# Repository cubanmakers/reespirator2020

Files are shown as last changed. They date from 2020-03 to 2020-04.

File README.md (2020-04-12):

# Reespirator 2020

Este repositorio pretende documentar y organizar los pasos para fabricar prototipos de  **Reespirator-2020**, un respirador open-source basado en el sistema de ventilación mecánica Jackson-Rees, diseñado y mejorado a partir de los prototipos elaborados por el equipo de Reesistencia Team para todas aquellas personas, organizaciones o empresas que quieran fabricarlo en cualquier parte del mundo.  

> ESTA DOCUMENTACIÓN ESTÁ EN ELABORACIÓN, COMPRUEBE REGULARMENTE LOS CAMBIOS, LAS PRIMERAS VERSIONES PUBLICADAS ESTÁN DESACTUALIZADAS. 

## Disclaimer
*Recuerde que un respirador es un dispositivo médico que sólo puede ser utilizado por personal cualificado y que un mal respirador o un respirador mal utilizado puede matar.*

La presente documentación **NO PERMITE CONSTRUIR UN RESPIRADOR FINAL**, sólo se publica para que se pueda fabricar PROTOTIPOS para investigación. 

## Info
*¿Qué es Reespirator 2020?*

El dispositivo Reespirator 2020 es un prototipo de sistema respirador de emergencia con elementos disponibles por la mayoría de las personas en cualquier parte del mundo, de rápida construcción y con la capacidad para mantener constantes ventilatorias aceptables en un paciente afecto de [Síndrome de Distrés Respiratorio Agudo](https://es.wikipedia.org/wiki/S%C3%ADndrome_de_dificultad_respiratoria_aguda) o SDRA.

Aunque el origen de Reespirator es España, debido a las regulaciones y validaciones necesarias para los productos médicos, y aunque Reespirator 23 de Reesistencia Team en el que se ha basado este nuevo diseño, ha superado varias pruebas preclínicas con animales, y de compatibilidad electromagnética, suponemos que este dispositivo nunca se llegará a fabricar masivamente en España, dónde afortunadamente lo peor de la crisis del COVID-19 parece que ya ha pasado (08/04/20); esperamos que este y otros diseños puedan ser útiles en otros países.

Aún así no nos damos por vencidos y seguiremos desarrollando el proyecto al menos en 2 versiones:

* Versión low cost (basada en Arduino y con caja de metacrilato, madera...)
* Versión pro (con un autómata PLC + un HMI y caja de chapa plegada en acero inoxidable)

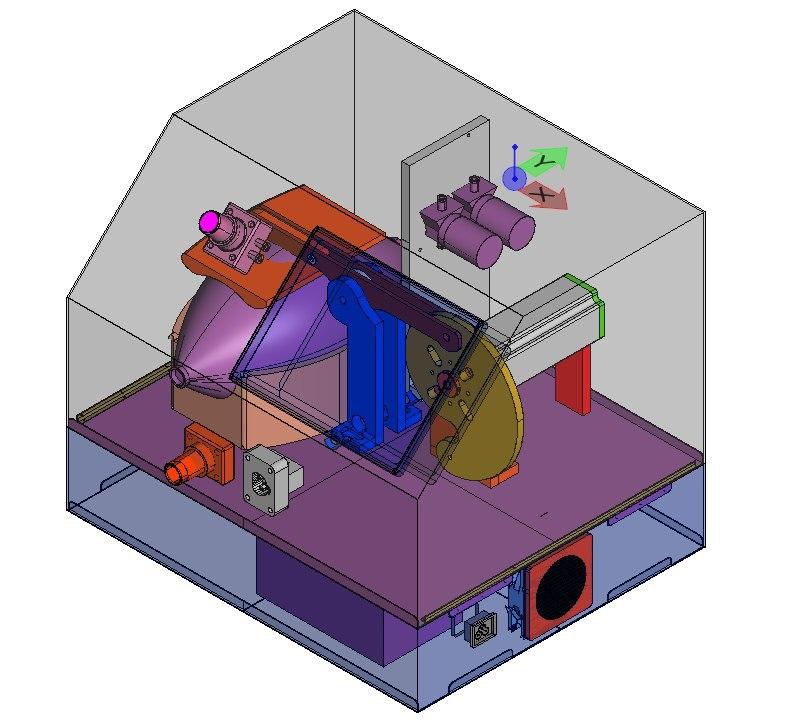
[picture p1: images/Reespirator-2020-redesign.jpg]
Reespirator


## Primeros pasos
Antes de montar un respirador lea toda la documentación posible e infórmese bien, si necesitas alguna aclaración abra un Issue y lo corregiremos en cuanto podamos. Si crees que puedes mejorar el diseño o el código envíanos un Pull request.

## [Estructura básica](https://gitlab.com/reespirator/reespirator-doc/-/blob/master/CASE.md)
Reespirator 2020 consta de una [caja](https://gitlab.com/reespirator/reespirator-doc/-/blob/master/CASE.md) diseñada para fabricarse mediante corte láser que contiene casi todos elementos del respirador en su interior. En el prototipo actual las piezas del prototipo se han diseñado para su corte por láser en metacrilato si bien la imagen anterior corresponde a la nueva evolución que podrá fabricarse también con chapa plegada.

## [Sistema neumático](https://gitlab.com/reespirator/reespirator-doc/-/blob/master/NEUMATIC.md)
El [sistema neumático](https://gitlab.com/reespirator/reespirator-doc/-/blob/master/NEUMATIC.md) del Reespirator 2020 está basado en un sistema Jackson-Rees. Reespirator 2020 utiliza además una serie de válvulas, sensores de presión y caudal y tubuladuras para hacer llegar al aire a los pulmones del paciente.

## [Mecánica](https://gitlab.com/reespirator/reespirator-doc/-/blob/master/MECHANIC.md)
El [sistema mecánico](https://gitlab.com/reespirator/reespirator-doc/-/blob/master/MECHANIC.md) pretende realizar los movimientos necesarios para realizar las maniobras de inspiración y espiración forzada del paciente mediante elementos mecánicos sustituyendo al personal humano que utilizaría el sistema de ventilación.

## [Electrónica](https://gitlab.com/reespirator/reespirator-doc/-/blob/master/ELECTRONICS.md)
La [electrónica](https://gitlab.com/reespirator/reespirator-doc/-/blob/master/ELECTRONICS.md) de control gestiona el movimiento del motor y los sensores que permiten realizar un control de lazo cerrado automatizado del sistema.
Además de la electrónica de control se emplea una electrónica adicional como interfaz de usuario que permite monitorizar diferentes señales del respirador y modificar en tiempo real diferentes configuraciones del mismo.

## [Firmware](https://gitlab.com/reespirator/reespirator-doc/-/blob/master/FIRMWARE.md)
El sistema de control necesita ser programado con un [firmware](https://gitlab.com/reespirator/reespirator-doc/-/blob/master/FIRMWARE.md) que permita hacer funcionar el dispositivo. Dicho programa se ha realizado conforme a las especificaciones de los especialistas médicos para realizar las funciones para las que el dispositivo fue diseñado.

## [Manual de usuario](https://gitlab.com/reespirator/reespirator-doc/-/blob/master/MANUAL.md)
El dispositivo Reespirator 2020 es un dispositivo médico y su uso sólo debe realizarse por personal especializado. Ofrecemos aquí un breve [manual de uso](https://gitlab.com/reespirator/reespirator-doc/-/blob/master/MANUAL.md) del mismo; pero es el personal sanitario el que sabe los parámetros que deben utilizarse para el tratamiento del paciente.

## Historia y principales cambios de esta versión

El proyecto Reespirator2020 toma como punto de partida el proyecto Reespirator 23 (o 24) v3 de **Reesistencia Team** a partir del cual realizamos un fork.

En esta nueva versión se incluyen principalmente los siguientes cambios:

 - Revisión y reestructuración en profundidad del códido de Arduino para asegurar la robustez de funcionamiento en todos los supuestos.
 - La recuperación del interfaz básico con LCD de 20x04 y elementos sencillos de control (4 pulsadores y un encoder con pulsador).
 - Establecimiento y documentación de una interfaz de comunicación serie que permite la utilización de sistemas (en adelante llamados Display+) de visualización, control y conectividad, que pueden ser utilizados como accesorios para aportar mejor usabilidad al sistema.
 - Se trabaja para estandarizar y popularizar los sensores y electro-válvulas para utilizar partes (comerciales o diseñadas) posibles de conseguir con la situación de emergencia actual y a precios accesibles.

## Repositorio temporal de trabajo para el código de Reespirator2020

El siguiente repositorio se está utilizando como fork de trabajo para transformar el código de Respirator 23 (o 24) v3 de Reesistencia Team (cuyo código se denominó 'batalla') en el código estable que se usará en Respirator 2020 de arduino, cuyo código se denominó  ['retaguardia'](https://gitlab.com/reespirator-arduino).

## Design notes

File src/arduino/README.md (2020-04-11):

# Reespirator

En la carpeta **rees_firmware** está el código de la última versión utilizada en Reespirator 23 para Arduino y la Beagle Bone con una pantalla táctil de 7" de WaveShare.

En la carpeta **test** encontrarás scripts de código que se utilizaron para hacer pruebas de distintos módulos y sensores utilizados en los primeros prototipos del Reespirator 23

## Resources

* [Arduino Reference](https://www.arduino.cc/reference/en/)
* [Arduino Best Practices and Gotchas](https://www.theatreofnoise.com/2017/05/arduino-ide-best-practices-and-gotchas.html)
* [C++ Best Practices (Gitbook)](https://lefticus.gitbooks.io/cpp-best-practices/content/)

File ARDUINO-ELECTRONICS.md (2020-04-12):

***Este documento describe la electrónica basada en Arduino. Si desea ver la versión para PLC, está disponible en el siguiente enlace: https://gitlab.com/reespirator/reespirator2020/-/blob/master/PLC-ELECTRONICS.md***

## Electrónica basada en Arduino
La electrónica de control gestiona el movimiento del motor y los sensores que permiten realizar un control de lazo cerrado automatizado del sistema. Además se emplea una electrónica adicional de interfaz de usuario que permite monitorizar diferentes señales del respirador y modificar en tiempo real diferentes configuraciones del mismo.

* En la versión de Arduino la electrónica de control está basada en un Arduino Mega y una serie de dispositivos sensores y actuadores conectados al mismo para realizar un sistema de control en lazo cerrado. 

* Estamos trabajando también en una versión basada en un autómata o PLC que fundamentalmente ha permitido realizar una correcta modelización del sistema.

En el prototipo actual la conexión de los distintos elementos se ha realizado sobre una shield de prototipado o breakout pero se está diseñando también una shield específica con los elementos necesarios para un ensamblado rápido de toda la electrónica, de forma que sólo sea necesario conectar los elementos sensores y actuadores mediante conectores.

Actualmente, se está trabajando el diseño de un PCB específico que integre la diversa electrónica que, en el prototipo, se ha realizado mediante módulos externos. Este desarrollo se irá liberando en el repositorio https://gitlab.com/reesistencia/reespirator-hardware

## Diagrama de Bloques del Sistema ##
En la siguiente figura se muestra de forma genérica el diagrama de bloques funcionales y elementos electrónicos del sistema:
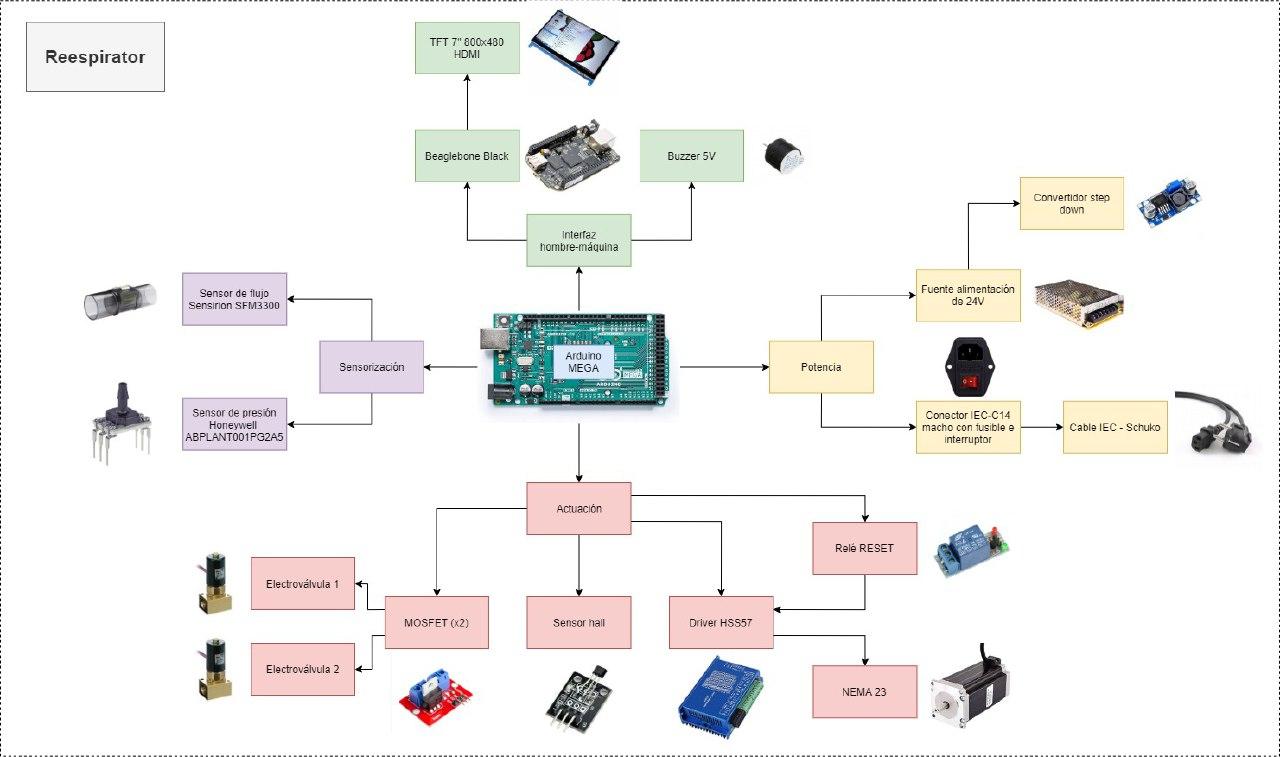
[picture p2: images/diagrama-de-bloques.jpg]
Diagrama de bloques


Según este esquema se puede observar que el sistema electrónico está compuesto por los siguientes bloques:

## Microcontrolador: 
Se ha empleado un Arduino Mega 2560 Rev3
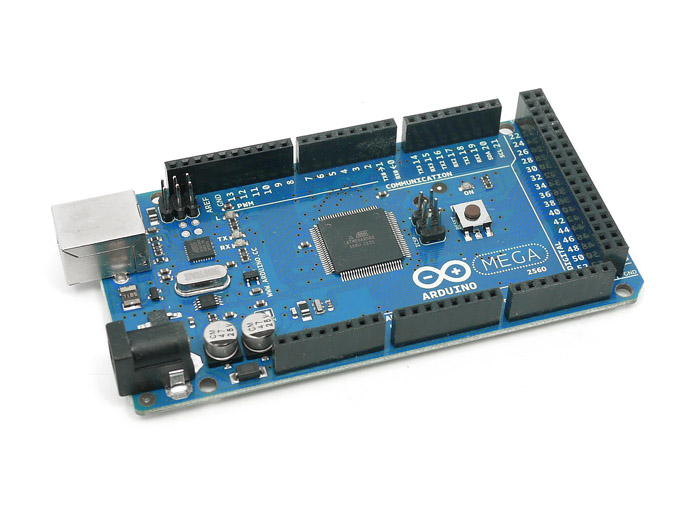
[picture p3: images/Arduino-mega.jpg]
Arduino Mega


## Etapa de alimentación:
Encargada de suministrar la energía necesaria para que todo el equipo funcione, está formada por los siguientes elementos:
	* La conexión a la red eléctrica se realizará mediante un conector IEC-C14 con fusible e interruptor.
	* La fuente de alimentación con entrada de 115-220V de corriente alterna de 50Hz/60Hz y salida 24Vdc.
	* Regulador step-down con salida de 5Vdc.
	
{Insertar esquema de conexión}

## Interfaz hombre-máquina: 
Permite la interacción entre el sistema y el usuario, mostrando la información necesaria o permitiendo actuar sobre los parámetros configurables. Para llevar a cabo esta tarea, la electrónica se ha diseñado para ofrecer dos formas principales de interacción con el usuario y que se describen a continuación: 
1. Interfaz de usuario básica: esta interfaz de usuario es la que se encuentra integrada en el diseño de la placa de la electrónica principal y que permitiría visualizar los parámetros básicos en un display sencillo (LCD 20x4), así como interactuar con el sistema.
2. Interfaz de usuario adicional, también denominada *Display+*: esta interfaz ajena a la placa principal, se comunicará con ésta para mostrar las gráficas o datos del sistema, de modo que el usuario final puede disponer de una interfaz de representación o visualización más completa. 

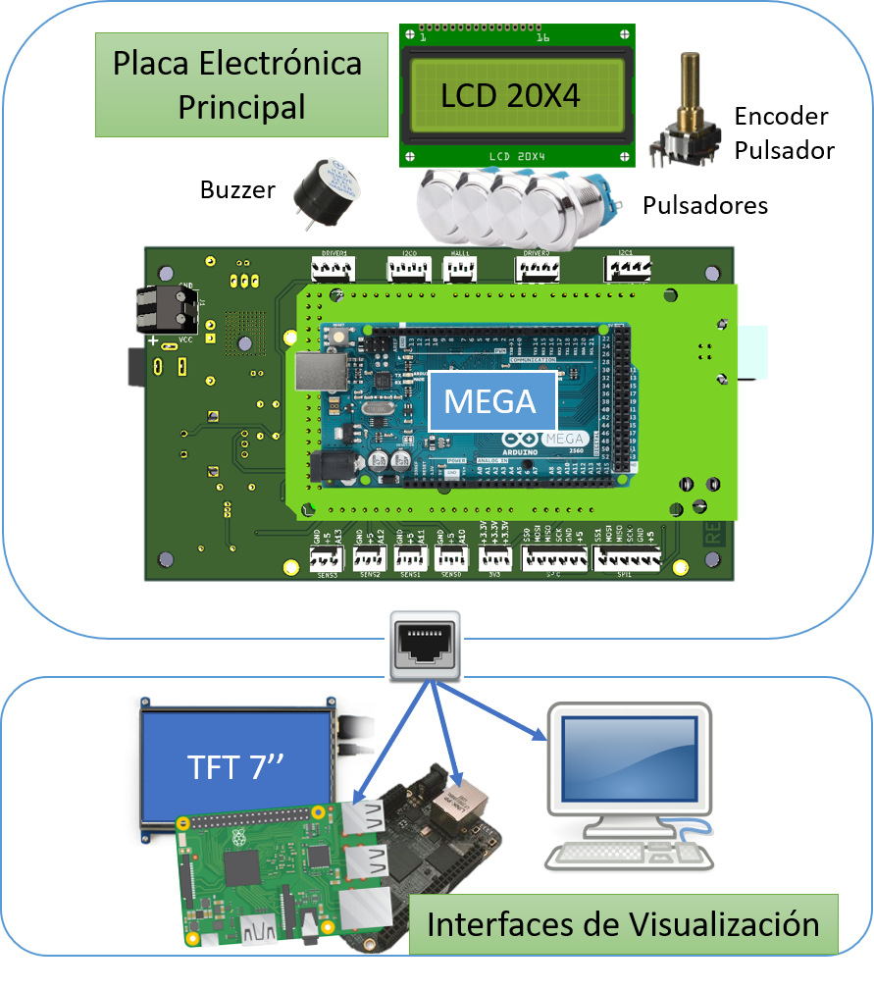
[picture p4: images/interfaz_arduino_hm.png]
Posibles Interfaces


Un ejemplo de este último sistema es con el que se han realizado las pruebas y que ha estado constituido por los siguientes elementos.

* PC embebido BeagleBone Black, que dispone de un procesador AM325x 1GHz Cortex A8, con 4GB de memoria flash y 512MB de memoria RAM DDR3.
* Pantalla TFT táctil de 7 pulgadas, con conexión HDMI, del fabricante ShareWave y resolución 800x480.
* Para la señalización de alarmas, se dispondrá de un zumbador acústico activo.

**Se insiste en que este es el sistema utilizado en el prototipo; pero se podría plantear la utilización de otros, aunque caso de ser aprobado este no tendría la validación necesaria en España.** 	

## Sistema de actuación y sensorización

* Se utilizarán motores NEMA, concretamente NEMA 24 que si bien no son tan comunes como los NEMA 23 dan un par motor suficiente. En los prototipos hemos utilizado motores de 4 Newton metros. En cualquier caso el uso de otro tipo de motores debe garantizar la suficiente presión sobre el globo del Jackson-Rees para producir el suficiente flujo ventilatorio. (Se hicieron pruebas con nema 17 y no daban sufiente par motor, seguramente algunos nema 23 puedan ser suficiente).

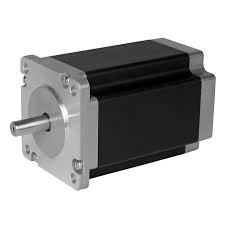
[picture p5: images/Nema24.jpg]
Nema 24 Motor Nema 24


* Los motores NEMA se controlarán con un driver para motores paso a paso que proporcione la intensidad suficiente para comandar el motor elegido. El modelo utilizado en el prototipo está en el siguiente esquemma, el ZDM-2HA865. Se ha elegido este modelo ya que puede controlar tanto el NEMA24 como motores más pequeños sin necesidad de cambiar todo el hardware.

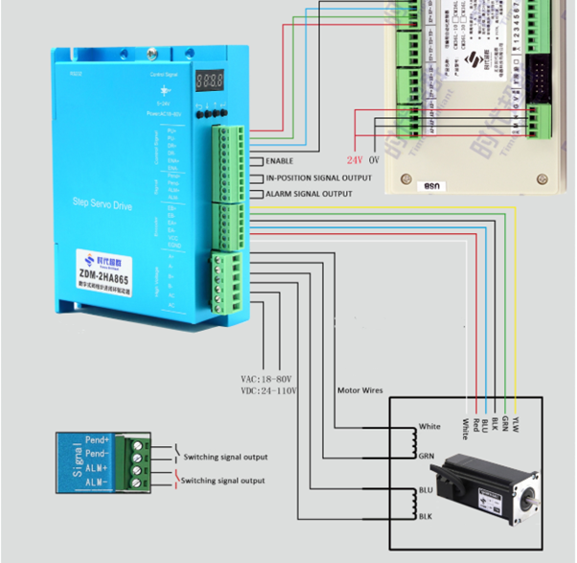
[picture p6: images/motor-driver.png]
Esquema de conexión Esquema de conexión del driver y el motor paso a paso


* Para monitorizar la posición inicial del sistema, se utilizará un sensor de efecto hall o un simple final de carrera, (aunque también se ha considerado la opción de un segundo sensor para evitar problemas).

* Electroválvula de 24V para el control de salida de aire del sistema neumático, (en el prototipo original se utilizaron 2 porque eran de un diámetro demasiado pequeño como para permitir un caudal apropiado).

* Sensor de caudal Sensirion SFM3300-AW para la medición del caudal en el espacio muerto del sistema de ventilación. Al ser una pieza que estará en contacto con el circuito de inspiración del paciente, se emplea un sensor homologado para aplicaciones médicas. (Si este modelo no estuviera disponible se pueden buscar sustitutos y con pequeñas modificaciones del código se podrían utilizar igualmente).

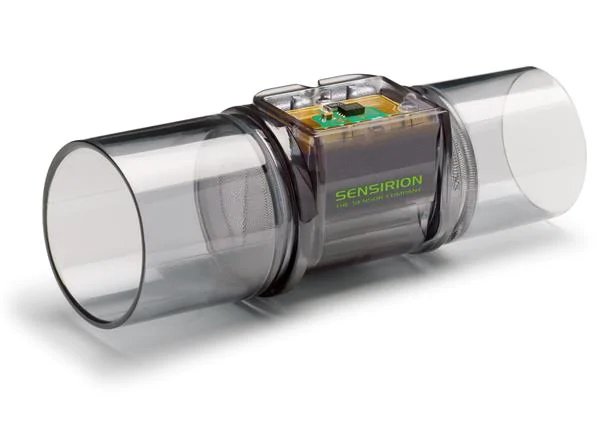
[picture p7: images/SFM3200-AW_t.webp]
Caudalímetro


* Sensor de presión diferencial para la diferencia de presión que existe entre el circuito inspiratorio y la presión ambiental. Se ha empleado el modelo ABPLANT001PG2A5 de Honeywell, que está homologado para aplicaciones médicas. (En versiones previas utilizamos 2 BME280 conectados por SPI). 

En la tabla siguiente podemos ver el pinout utilizado en el prototipo:

| USO                   |PIN |
| --------------------- | -- |
| PIN_STEPPER_STEP      |  6 |
| PIN_STEPPER_DIRECTION |  7 | 
| PIN_STEPPER_EN STEP   |  8 |
| PIN_STEPPER_ALARM     |  3 | 
| PIN_BUZZ              | 11 |
| PIN_STEPPER_ENDSTOP   |  2 | 
| PIN_SOLENOID          | 39 |
| PIN_RELAY             | 25 | 

## Diseño de la Electrónica Principal ##

El diseño electrónico de la placa principal, se ha dividido en diferentes secciones atendiendo a las especificaciones y requerimientos hardware indicados anteriormente en el [Repositorio](https://gitlab.com/reesistencia/reespirator-hardware "Repositorio Hardware"). Para acceder a una descripción de cada una de estas partes, seguir el siguiente enlace.

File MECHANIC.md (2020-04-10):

El sistema mecánico de Reespirator utiliza un motor Nema 23/24 que hace oscilar una leva con forma de caracol y esta mueve a su vez una palanca que bascula haciendo moverse al empujador que aprieta sobre el globo del Jackson-Rees.

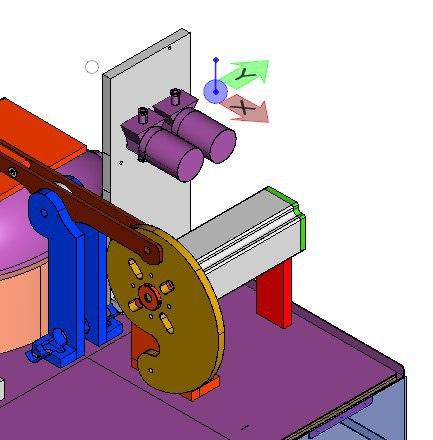
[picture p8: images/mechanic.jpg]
Detalle Detalle de la leva, el motor y la palanca


La parte mecánica consta de:

* Una leva fabricada en metacrilato de 8mm. con un casquillo adaptador, fabricado en acero.

* Un balancín formado por 2 piezas de metacrilato de 4 mm. Dispone de un rodamiento 608ZZ, que entra en contacto con la leva y pivota sobre un tornillo M8 que lo ancla a la estructura de la caja, y en su parte final está fijado a una pala, impresa en 3D, con dos tornillos M5.
* La carcasa, que contiene todo el dispositivo está fabricada en metacrilato de 10mm, dispone además de un embellecedor, cortado en láser de metacrilato de 4mm para protección mecánica.

* Además, dispone de una [cuna](https://gitlab.com/reespirator/reespirator2020/-/blob/master/files/stl/cuna.stl "Cuna impresa en 3D para alojar el balón del Jackson-Rees") impresa en 3D donde se aloja el balón respirador de Jackson Rees.

* El sistema utiiza también una [pala o empujador](https://gitlab.com/reespirator/reespirator2020/-/blob/master/files/stl/empujador_v3.stl "Cuna impresa en 3D para alojar el balón del Jackson-Rees") impresa en 3D que empuja el balón respirador para insuflar el aire al paciente. 

Estas 2 piezas se imprimirán en la mayor calidad posible, pues ambas quedan en contacto con el globo y no deben tener fallos que puedan dañar el mismo.

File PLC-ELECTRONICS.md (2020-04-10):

***Este documento describe la electrónica basada en PLC. Si desea ver la versión para Arduino, está disponible en el siguiente enlace: https://gitlab.com/reespirator/reespirator2020/-/blob/master/ARDUINO-ELECTRONICS.md***

## Electrónica con PLC 
La electrónica de control gestiona el movimiento del motor y los sensores que permiten realizar un control de lazo cerrado automatizado del sistema. Además se emplea una electrónica adicional de interfaz de usuario que permite monitorizar diferentes señales del respirador y modificar en tiempo real diferentes configuraciones del mismo.

El diagrama de bloques funcionales y elementos electrónicos del sistema se muestra en la siguiente figura:
_PENDIENTE_

### PLC

Según este esquema podemos ver que el sistema electrónico está compuesto por un autómata SIEMENS Simatic S7-1200 CPU 1215c al que se conectan los sensores y actuadores del sistema. Opcionalmente se puede suministrar la misma CPU en su versión SAFETY CAT-IV/SIL 3 mejorando grandemente tiempo medio entre fallos (mtbf), que ya de por si es bajo.

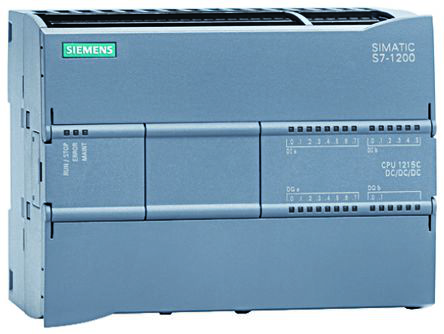
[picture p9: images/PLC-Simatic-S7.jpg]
SIEMENS Simatic S7-1200


### Display táctil

Dispone de un display táctil SIEMENS TP700, con las siguientes capacidades: registro de alarmas, histórico de datos, monitorización remota con gestión de usuario y password para evitar accionamientos no autorizados. El gestor de accesos indica en la pantalla si se está operando sobre la pantalla en remoto. Dispone de una memoria SD para almacenamiento de datos de alarmas y datos de trabajo.

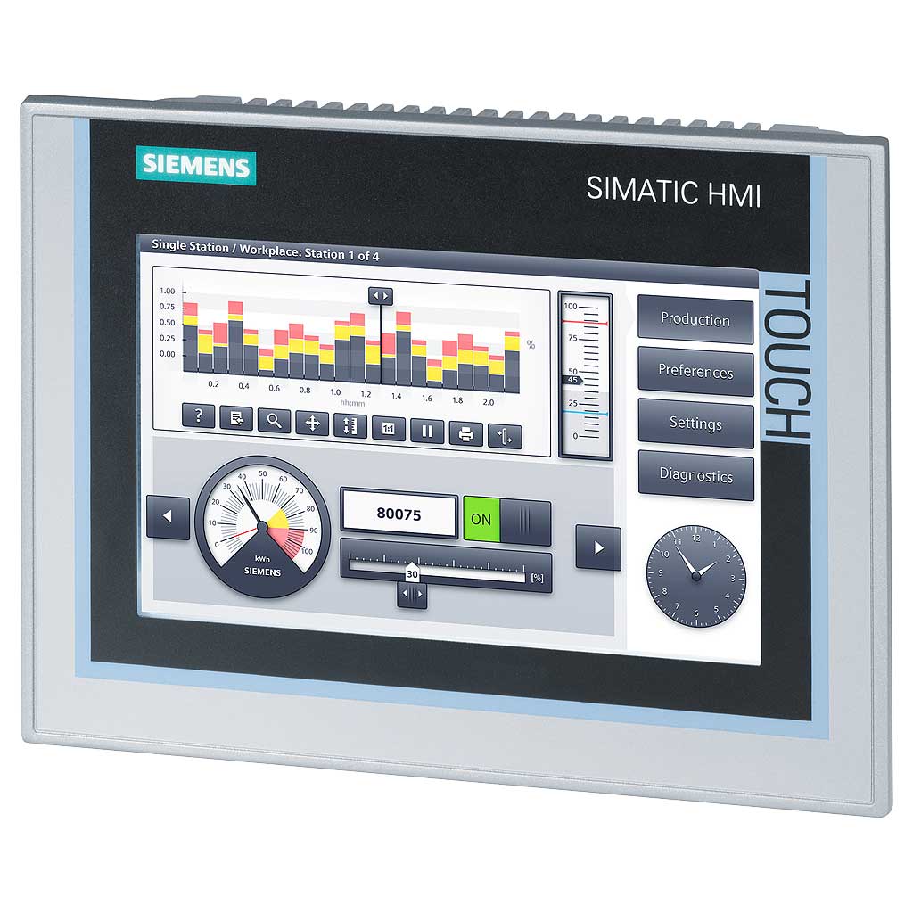
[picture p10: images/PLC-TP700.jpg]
SIEMENS TP700


### Etapa de alimentación:
El dispositivo está preparado para conectarse a la red eléctrica de 110-230V de corriente alterna y utiliza una fuente de alimentación principal de baja tensión de 24V de corriente continua capaz de suministrar al menos 15A. Para mantener su funcionamiento en caso de fallo de la alimentación debe emplearse un SAI o bien solicitar alimentación auxiliar de 24Vdc.

### Sistema de actuación y sensorización

* Se utilizarán motores NEMA, concretamente NEMA 24 que si bien no son tan comunes como los NEMA 23 dan un torque suficiente. En los prototipos hemos utilizado motores de 4,2N/m. En cualquier caso el uso de otro tipo de motores debe garantizar la suficiente presión sobre el globo del Jackson-Rees para producir el suficiente flujo ventilatorio.

Nema 24 Motor Nema 24

* Los motores NEMA se controlarán con un driver HSS57. Se ha elegido este modelo ya que puede controlar tanto el NEMA24 como motores más pequeños sin necesidad de cambiar todo el hardware.

Esquema de conexión Esquema de conexión del driver y el motor paso a paso

* Para monitorizar la posición inicial del sistema, se utilizará un sensor de efecto hall o un simple final de carrera, (aunque también se ha considerado la opción de un segundo sensor para evitar problemas).

* Electroválvula de 24V para el control de salida de aire del sistema neumático, (en el prototipo original se utilizaron 2 porque eran de un diámetro demasiado pequeño como para permitir un caudal apropiado).

* Sensor de caudal Sensirion SFM3300-AW para la medición del caudal en el espacio muerto del sistema de ventilación. Al ser una pieza que estará en contacto con el circuito de inspiración del paciente, se emplea un sensor homologado para aplicaciones médicas. (Si este modelo no estuviera disponible se pueden buscar sustitutos y con pequeñas modificaciones del código se podrían utilizar igualmente).

Caudalímetro

* Sensor de presión diferencial para la diferencia de presión que existe entre el circuito inspiratorio y la presión ambiental. Se ha empleado el modelo ABPLANT001PG2A5 de Honeywell, que está homologado para aplicaciones médicas. (En versiones previas utilizamos 2 BME280 conectados por SPI).

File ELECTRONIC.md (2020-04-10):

## Electrónica
La electrónica de control gestiona el movimiento del motor y los sensores que permiten realizar un control de lazo cerrado automatizado del sistema. Además se emplea una electrónica adicional de interfaz de usuario que permite monitorizar diferentes señales del respirador y modificar en tiempo real diferentes configuraciones del mismo.

* En la versión de Arduino la electrónica de control está basada en un Arduino Mega y una serie de dispositivos sensores y actuadores conectados al mismo para realizar un sistema de control en lazo cerrado. 

* Estamos trabajando también en una versión basada en un autómata o PLC que fundamentalmente ha permitido realizar una correcta modelización del sistema.

En el prototipo actual la conexión de los distintos elementos se ha realizado sobre una shield de prototipado o breakout pero se está diseñando también una shield específica con los elementos necesarios para un ensamblado rápido de toda la electrónica, de forma que sólo sea necesario conectar los elementos sensores y actuadores mediante conectores.

Actualmente, se está trabajando el diseño de un PCB específico que integre la diversa electrónica que, en el prototipo, se ha realizado mediante módulos externos. Este desarrollo se irá liberando en el repositorio https://gitlab.com/reesistencia/reespirator-hardware

El diagrama de bloques funcionales y elementos electrónicos del sistema se muestra en la siguiente figura:
Diagrama de bloques

Según este esquema podemos ver que el sistema electrónico está compuesto por:

## Microcontrolador: se ha empleado un Arduino Mega 2560 Rev3
Arduino Mega

## Etapa de alimentación:
	* La conexión a la red eléctrica se realizará mediante un conector IEC-C14 con fusible e interruptor.
	* Fuente de alimentación con entrada de 220Vac/50Hz y salida 24Vdc.
	* Regulador step-down (LM2596, por ejemplo), con salida de 12Vdc.

{Insertar esquema de conexión}

## Interfaz hombre-máquina:

	* PC embebido BeagleBone Black, que dispone de un procesador AM325x 1GHz Cortex A8, con 4GB de memoria flash y 512MB de memoria RAM DDR3.

	* Pantalla TFT táctil de 7 pulgadas, con conexión HDMI, del fabricante ShareWave y resolución 800x480.

	* Para la señalización de alarmas, se dispondrá de un zumbador acústico activo.

Insistimos en que este es el sistema utilizado en nuestro prototipo; pero se podría plantear la utilización de otros aunque caso de ser aprobado este no tendría la validación necesaria.

## Sistema de actuación y sensorización

	* Se utilizarán motores NEMA, concretamente NEMA24.

	* Los motores NEMA se controlarán con un driver HSS57. Se ha elegido este modelo ya que puede controlar tanto el NEMA24 como motores más pequeños sin necesidad de cambiar todo el hardware.
	![Esquema de conexión](Arduino Mega Esquema de conexión del driver y el motor paso a paso

	* Para monitorizar la posición inicial del sistema, se utilizará un sensor de efecto hall.

	* Electroválvula para el control de salida de aire del sistema neumático.

	* Sensor de caudal Sensirion SFM3300-AW para la medición del caudal en el espacio muerto del sistema de ventilación. Al ser una pieza que estará en contacto con el circuito de inspiración del paciente, se emplea un sensor homologado para aplicaciones médicas.

	* Sensor de presión diferencial para la diferencia de presión que existe entre el circuito inspiratorio y la presión ambiental. Se ha empleado el modelo ABPLANT001PG2A5 de Honeywell, que está homologado para aplicaciones médicas. (En versiones previas utilizamos 2 BME280 por SPI).

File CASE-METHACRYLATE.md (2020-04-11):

## Estructura básica en metacrilato o MDF
Reespirator 2020 puede fabricarse como ya hemos comentado en 2 versiones diferentes. 
La caja puede fabricarse también de dos formas distintas mediante corte láser o fresado de metacrilato o madera y mediante plegado de chapa-

* La versión de metacrilato / madera / mdf es de tipo machiembrado como la que aparece en las siguiente figuras para facilitar su montaje. 

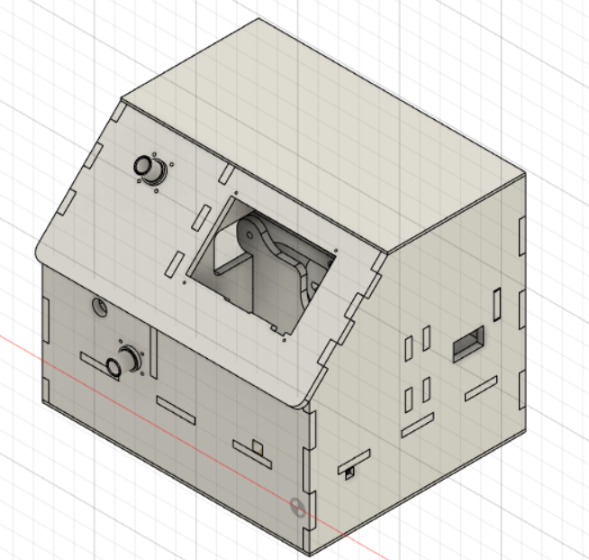
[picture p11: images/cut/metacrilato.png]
Caja completa


> La siguiente información es de una primera versión de Reespirator 2020 se está actulizando toda la documentación a medida que la vamos teniendo disponible. **Por favor, no fabricar todavía.** Además debe tenerse en cuenta que al fabricar puede que haya ajustar una décima de milímetro las medidas para el corte.

Reespirator 2020 consta de una caja diseñada para fabricarse mediante corte láser modificados a partir de los diseños originales de Reesistencia Team y que contiene casi todos elementos del respirador en su interior. 

Los archivos provisionales para su fabricación mediante corte láser o fresado (CNC) se encuentra en el directorio [/files/cut](https://gitlab.com/reespirator/reespirator2020/-/tree/master/files/cut "files/cut").

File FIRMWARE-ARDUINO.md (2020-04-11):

## Firmware Arduino

El firmware para el Arduino Mega está en el repositorio [reespirator-firmware](https://gitlab.com/reesistencia/reespirator)

Otro grupo de programadores está reorganizando y refactorizando el código para hacerlo más sólido:
[https://gitlab.com/reespirator-arduino/reespirator](https://gitlab.com/reespirator-arduino/reespirator)

Hay que tener en cuenta que para la versión con Arduino se han barajado al menos 3 configuraciones distintas:

* 1 LCD de 20 caracteres x 4 líneas y un encoder.
* 1 LCD de 20 caracteres x 4 líneas y cuatro encoders o 1 encoder y 4 botones.
* 1 Pantalla gráfica táctil con otro dispositivo externo como una beagle-bone, una Raspberry Pi o un portátil o PC de escritorio conectados por puerto serie.

El software para la Beagle-bone y la pantalla utilizadas en el prototipo Reespirator 23 fue programado en Python y está disponible en el repositorio [reespirator-beagle-touch](https://gitlab.com/reesistencia/reespirator-beagle-touch) 

En otros grupos de Telegram se ha logrado hacer funcionar este mismo código de visualización en un portátil y en una Raspberry Pi.

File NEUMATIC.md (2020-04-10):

## Sistema neumático
Basado en un sistema [Jackson-Rees](https://en.wikipedia.org/wiki/Breathing_circuit), **Reespirator** es un respirador que además del mencionado sistema médico Jackson-Rees utiliza una serie de elementos neumáticos utilizados para entubar al paciente y para controlar sus flujos de respiración inspiratorios y espiratorios.

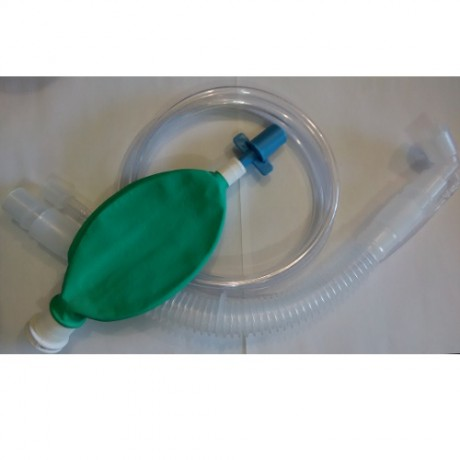
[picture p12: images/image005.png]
Sistema Jakson-Rees Sistema Jackson-Rees


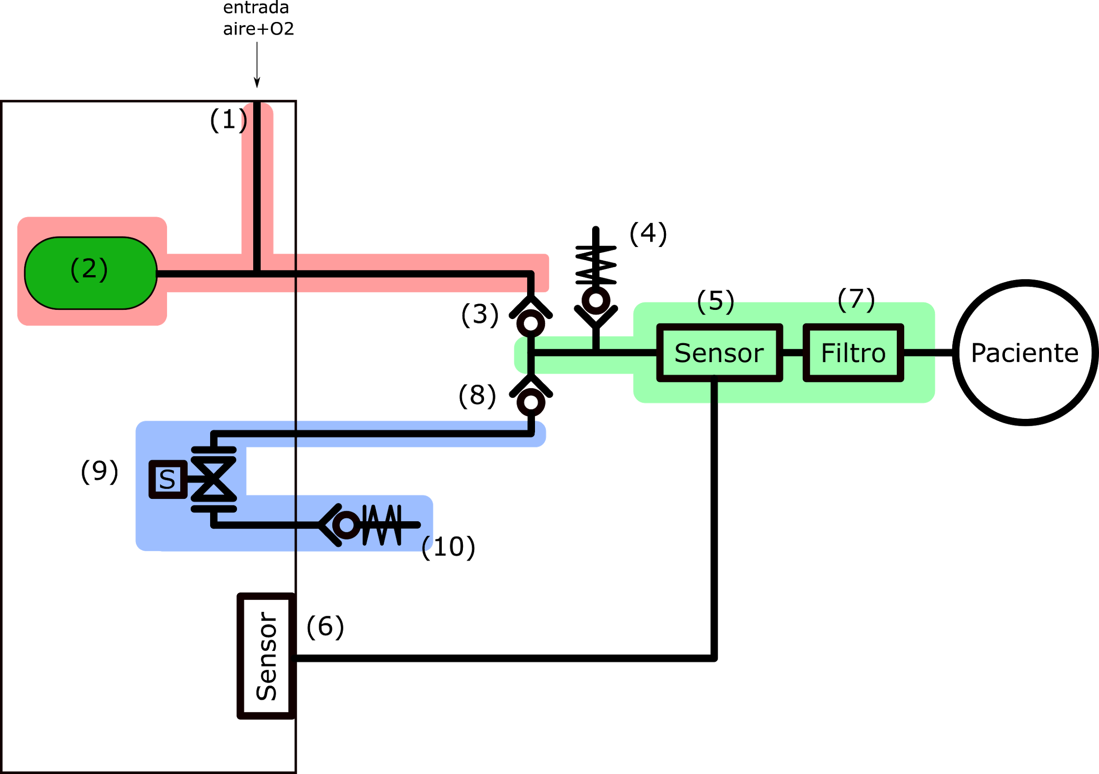
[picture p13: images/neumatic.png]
Esquema neumático


El circuito neumático completo está compuesto por tres secciones:
* Circuito de inspiración, resaltado en rojo en el diagrama
* Circuito de paciente, resaltado en verde en el diagrama
* Circuito de espiración, resaltado en azul en el diagrama

El circuito de inspiración (rojo) está compuesto por los siguientes elementos:
Línea de entrada de aire+O2 (1) proporciona el gas que respira el paciente. Deberá proporcionar un caudal en exceso sobre el caudal medio programando. La mezcla se realizará de forma externa al sistema, dependiendo de las capacidades de cada hospital:
En caso de que sólo exista una botella de oxígeno, se podría hacer una mezcla usando una válvula de venturi
En caso de que existan líneas separadas de oxígeno y aire, se podrá hacer una mezcla con válvulas y rotámetros para controlar la proporción de mezcla.
Balón del Mapleson o Jackson Rees (2) es accionado por el mecanismo motorizado y leva durante el ciclo de inspiración. Durante el ciclo de espiración la leva vuelve a posición de reposo para permitir que la línea de entrada (1) rellene el balón.

El circuito de inspiración (rojo) se comunica con el circuito de paciente (verde) por medio de la válvula anti-retorno (3).

El circuito de paciente (verde) está compuesto por los siguientes elementos:
Válvula de alivio de presión (4) o de seguridad: protege al paciente de sobrepresiones que pudieran suceder en el circuito, por un comportamiento incorrecto del respirador o por espasmos u otros movimientos causados por el propio paciente durante el ciclo de inspiración. La normativa indica que esta válvula de seguridad debe ser menor de 80 cmH2O, y lógicamente ha de ser mayor que la presión inspiratoria máxima que se desee que tenga el sistema, que típicamente rondará los 40 cmH2O.
Bloque de sensor (5): proporciona una medida de caudal y de presión en el circuito de paciente. Su cableado de medida se conecta a la caja del respirador mediante un conector Estará conectado a la caja del respirador a un terminal de conexión de los sensores (6). La medida de caudal se realiza mediante el método de placa orificio. Se mide la pérdida caída de presión del flujo del aire al atravesar un orificio de características conocidas. Se utiliza un sensor de presión diferencial que mide la diferencia de presiones, y también un sensor manométrico (o gauge) que proporciona una medida de la presión. El uso de estos sensores de presión para medir el caudal tiene como principales ventajas su reducido coste y alta disponibilidad en comparación con sensores de tipo caudalímetro. Inicialmente se contemplan dos opciones, en cuanto a la forma en que se realiza la medida de caudal:
Por placa orificio. Se mide la pérdida caída de presión del flujo del aire al atravesar un orificio de características conocidas. La conexión de este punto a la caja del respirador se puede realizar por medio de dos tubos, estando los sensores en el interior del respirador. Se necesita un sensor de presión diferencial que mida la dicha diferencia de presiones, y también un sensor manométrico (o gauge) que proporciona una medida de la presión. Como ventaja, se simplifica el número de elementos externos a la caja del respirador (dos tubos), y su coste y disponibilidad, dado que los sensores de presión son abundantes y baratos.
Caudalímetro tipo mass-flow. Produce una medida directa del caudal. Requiere la conexión de cables de alimentación y comunicación desde la caja del respirador hasta el sensor. Adicionalmente es necesario obtener una medida de presión que típicamente el sensor de caudal no proporciona. Esta medida se obtendría mediante un sensor manométrico o gauge, que podría estar situado junto al medidor de caudal (aprovechando que de todas maneras hay que llevar conexiones eléctricas hasta este punto) o podría estar en la caja del respirador, comunicado con el circuito de paciente mediante un tubo. 
Filtro (7): su función es purificar el aire tanto a la entrada como a la salida del paciente.  

El circuito de paciente (verde) se comunica con el circuito de espiración (azul) por medio de la válvula anti-retorno (8).

El circuito de espiración (azul) está compuesto por los siguientes elementos:
Electroválvula (9)
Válvula PEEP regulable (10): su objetivo es el mantenimiento de una presión mínima en el sistema durante la espiración para evitar el colapso pulmonar. Esta válvula se regula automáticamente para conseguir la presión PEEP establecida por el médico en el display del respirador. es de regulación automática mediante un sistema de electroválvulas, lo que permite al médico instaurarlo en el propio display.

Biocompatibilidad
Todos los elementos del circuito de inspiración (rojo) y circuito de paciente (verde), incluidas las válvulas anti-retorno (3) y (8) deben ser medical-grade, ya que el aire que circula por ellos es insuflado en los pulmones del paciente

El aire que circula los elementos del circuito de espiración (azul) nunca retorna a los pulmones del paciente gracias a la válvula anti-retorno (8), por lo cual no es necesario que sean medical-grade.

Reusabilidad
Los elementos del circuito de inspiración (rojo) se ven protegidos del aire espirado por el paciente por la válvula anti-retorno (3), por lo cual no se contaminarán y se pueden reutilizar.

Los elementos del circuito de espiración (azul) sí son contaminados, pero el aire en contacto con ellos nunca debería entrar en contacto con un nuevo paciente, gracias a la válvula anti-retorno (8), con lo cual son, también, reutilizables.

Los elementos del circuito de paciente (verde) son contaminados y su uso en un nuevo paciente sin previa esterilización no debería permitirse (salvo que la confianza en el filtro (7) sea plena). El bloque sensor y sus sensores también se contaminan y deberán ser sustituidos para cada nuevo paciente. Si se opta por una opción de sensores en la que dichos sensores están dentro de la caja del respirador, pero conectados por tubo(s) al circuito de paciente,  estos sensores, siendo estrictos, también deberían ser reemplazado o esterilizados.

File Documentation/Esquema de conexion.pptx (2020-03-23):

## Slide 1

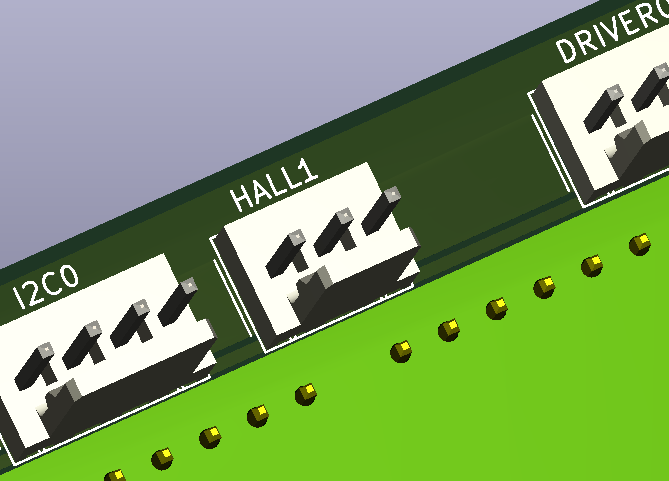
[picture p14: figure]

Señal

+5V

GND

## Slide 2

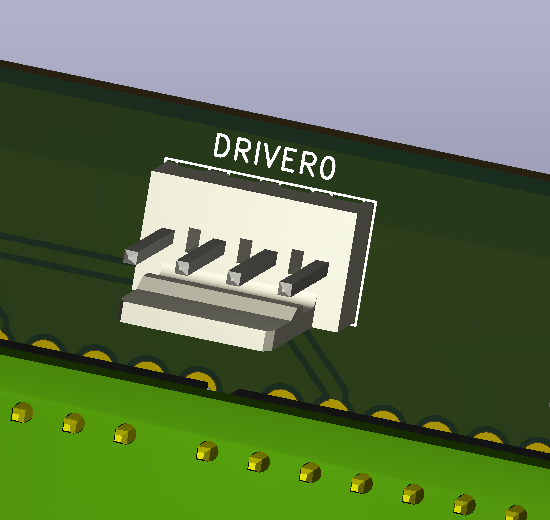
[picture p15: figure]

PUL

GND

ENA

DIR

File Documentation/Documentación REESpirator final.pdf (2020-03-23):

### Sistema electrónico Reespirator

### 1. Introducción

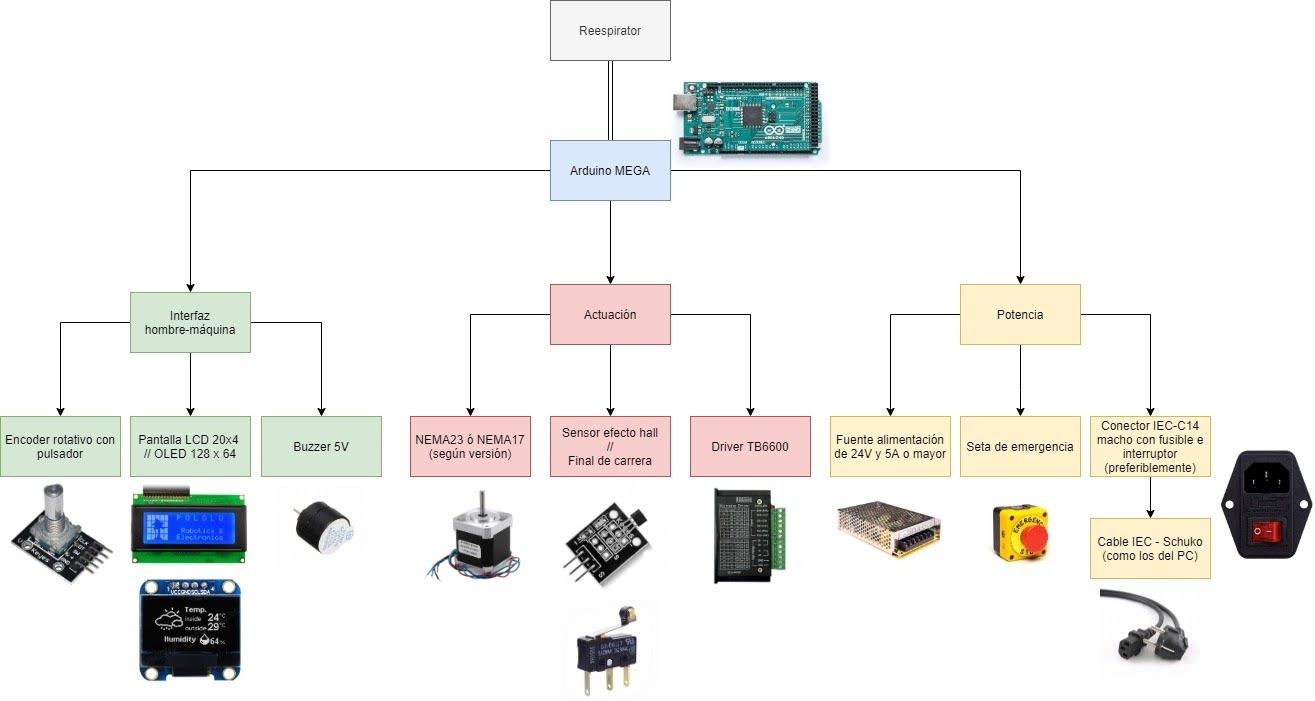
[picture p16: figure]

La PCB se ha diseñado de manera que se pueda pinchar encima de un Arduino MEGA e integra en la propia PCB un display LCD, un encoder rotativo con pulsador y un buzzer, así como conectores para los diferentes módulos, que se describen a continuación.

Se ha separado el sistema en 4 grupos, que forman parte del Reespirator:
- Microcontrolador: se ha optado por un Arduino MEGA
- Interfaz hombre-máquina (completamente integrada en la placa)
- Se utilizará un display de 20x4 con interfaz paralela. Opcionalmente se puede colocar una pantalla gráfica OLED de 128x64.
- Para navegar por los menús y configurar parámetros se utilizará un encoder rotativo con pulsador.
- Para avisar de alguna alarma se utilizará un zumbador activo.
- Sistema de actuación
- Se utilizarán motores NEMA, concretamente NEMA17 o NEMA23 según el modelo de Reespirator a fabricar.
- Los motores NEMA se controlarán con un driver TB6600. Se ha elegido este modelo ya que puede controlar tanto el NEMA23 como motores más pequeños sin necesidad de cambiar todo el hardware.
- Para monitorizar la posición inicial del sistema, se utilizará un sensor de efecto hall o un final de carrera mecánico, según la disponibilidad. Se recomienda el uso de un sensor de efecto hall o de un sensor óptico ya que, al ser sin contacto, no hay problemas de ciclos de funcionamiento máximos.
- Sistema de potencia / eléctrico
- Para alimentar todo el aparato se utilizará una fuente de alimentación a 24V con una salida igual o superior a 5A.

Rev 2

- Para alimentar el Arduino se utilizará un regulador de tensión LM7812 integrado en la propia placa, con proteccion ante polaridad inversa. Se podrá conectar tanto con un screw-block terminal como con un jack de alimentación. El LM7812 se ha colocado tumbado y en contacto con la placa para mejorar la disipación térmica. Si se tienen problemas de disipación se puede sustituir por un convertidor DC/DC VXO78012, totalmente compatible en pines.
- Se utilizará una seta para poder cortar la alimentación a la máquina en caso de emergencia.
- La conexión a la red eléctrica se realizará mediante un conector IEC-C14 macho con fusible e interruptor.

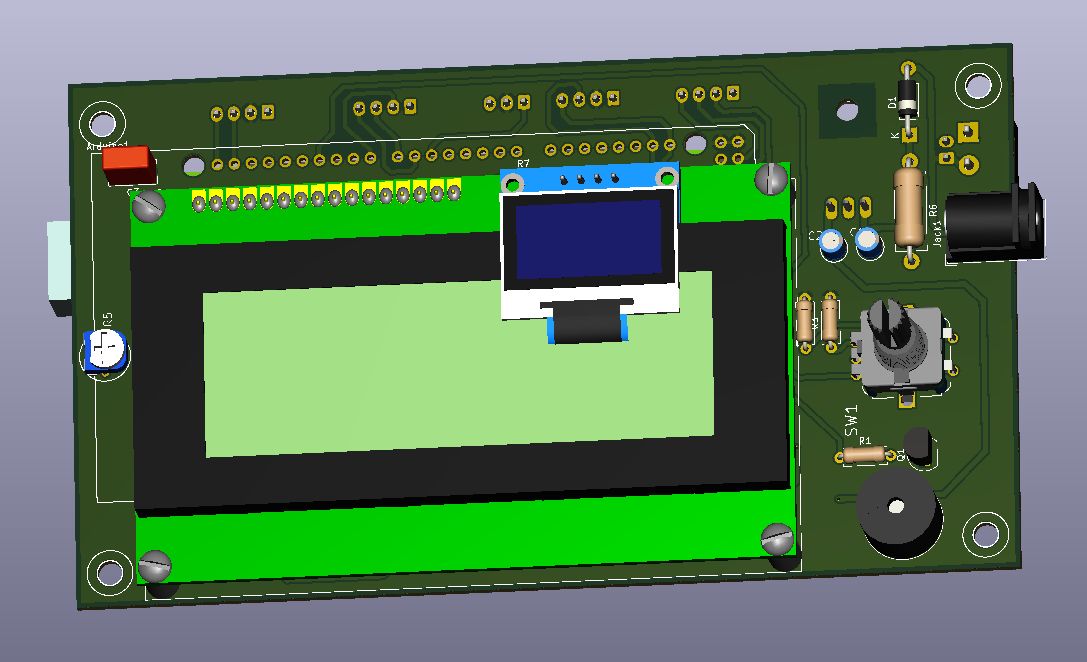
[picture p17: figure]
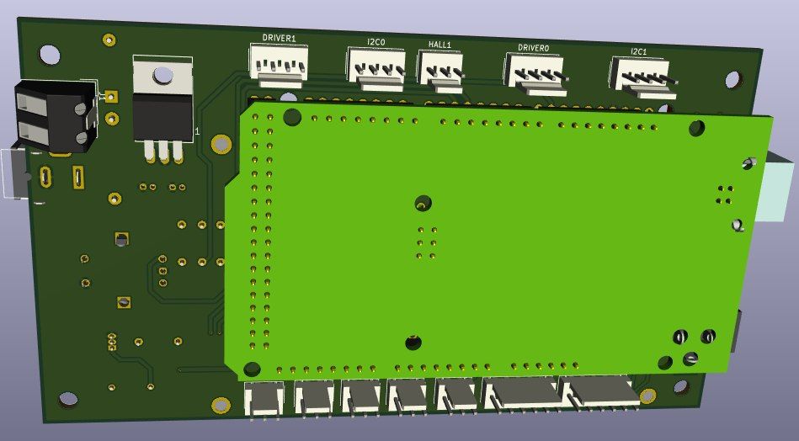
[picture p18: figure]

### 2. Conexión de los módulos

- Sensor efecto hall / final de carrera

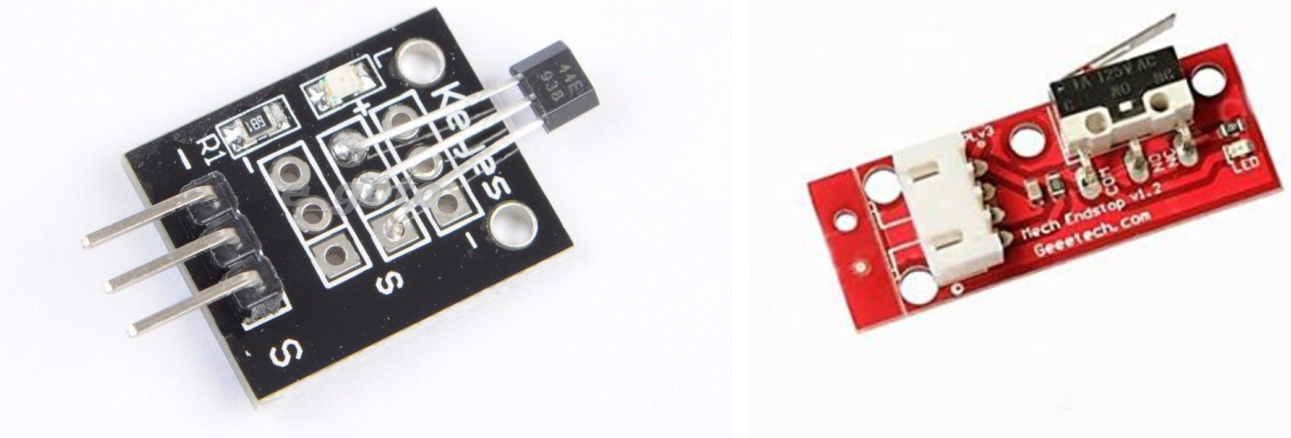
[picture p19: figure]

Se conectará al conector marcado como HALL en la parte trasera de la PCB, mediante un conector MOLEX 10-11-2033, aunque es compatible con otros headers con 2.54 mm de pitch (incluso se podrían usar cables Dupont o similares).

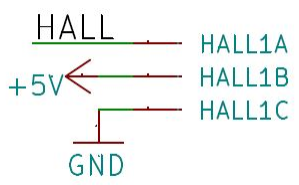
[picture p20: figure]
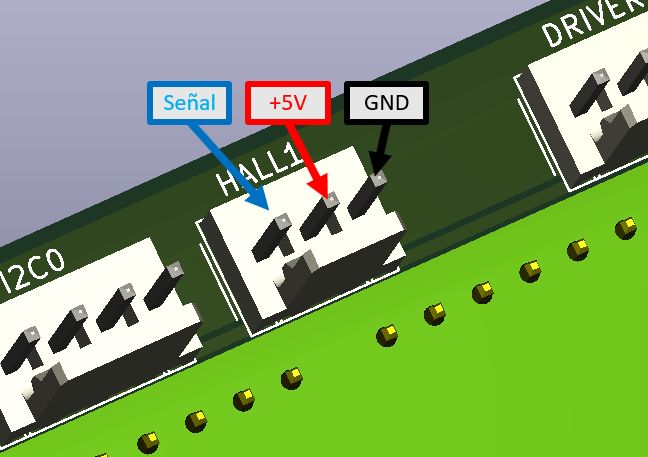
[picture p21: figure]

- Driver TB6600 + NEMA

Señales de control: Se conectará al conector marcado como DRIVER0 en la parte trasera de la PCB, mediante un conector MOLEX 10-11-2043, aunque es compatible con otros headers con 2.54 mm de pitch (incluso se podrían usar cables Dupont o similares).

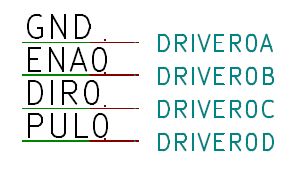
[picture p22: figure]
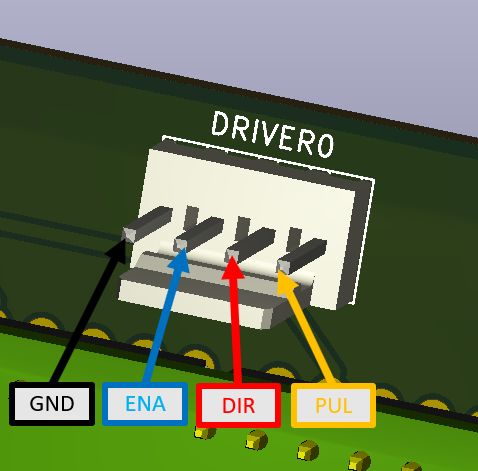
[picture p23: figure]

Señales del motor: Conectados a un motor paso a paso. Los colores del cableado pueden cambiar según el motor utilizado, consultar el datasheet del motor antes de poner la máquina en marcha.
- B- y B+: conectado a la fase B del motor paso a paso
- A- y A+: conectado a la fase A del motor paso a paso

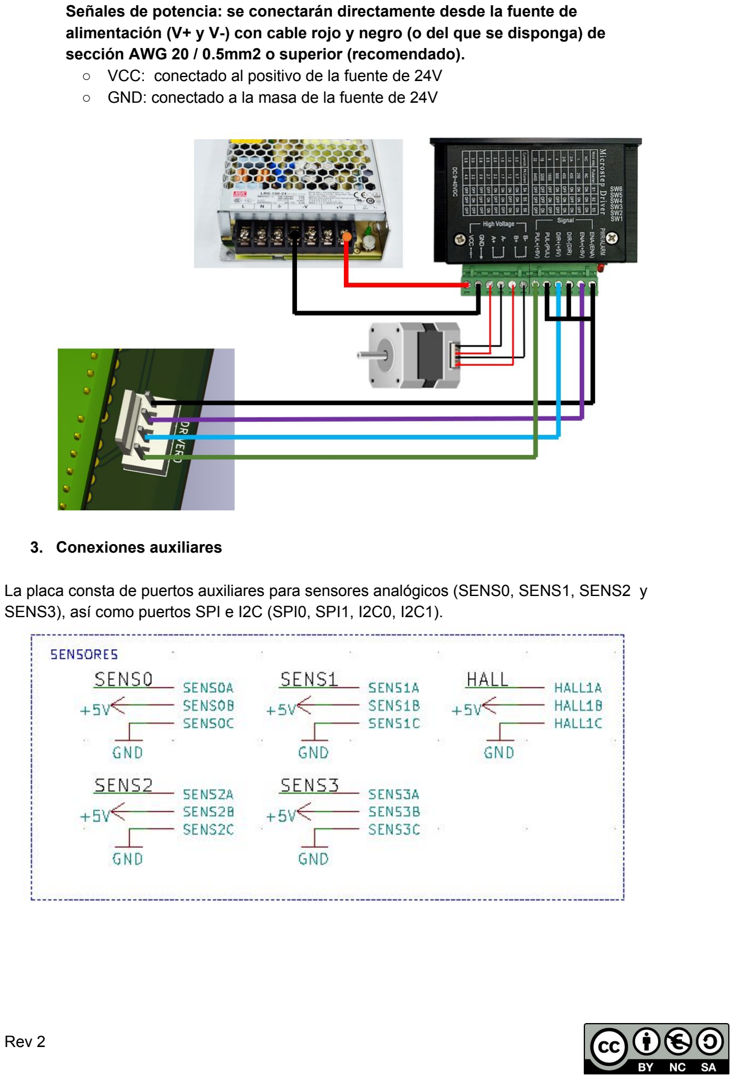
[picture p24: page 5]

Señales de potencia: se conectarán directamente desde la fuente de alimentación (V+ y V-) con cable rojo y negro (o del que se disponga) de sección AWG 20 / 0.5mm2 o superior (recomendado).
- VCC: conectado al positivo de la fuente de 24V
- GND: conectado a la masa de la fuente de 24V

### 3. Conexiones auxiliares

La placa consta de puertos auxiliares para sensores analógicos (SENS0, SENS1, SENS2 y SENS3), así como puertos SPI e I2C (SPI0, SPI1, I2C0, I2C1).

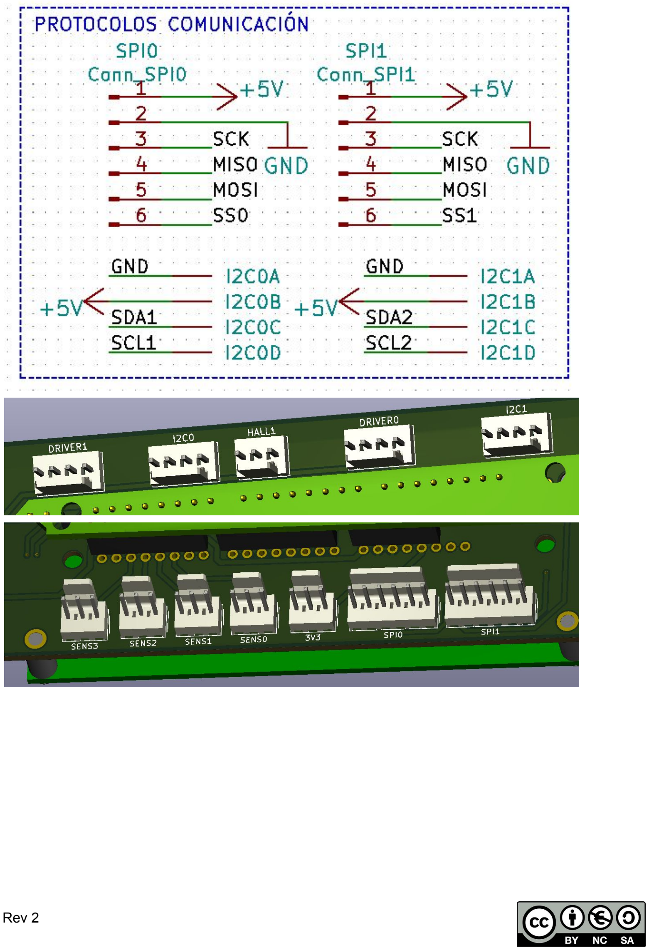
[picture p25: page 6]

La distribución de pines en el Arduino MEGA es la siguiente:


### 4. Conexionado de corriente alterna

El conexionado de la parte de 230 VAC se debe realizar con extremo cuidado. Para las conexiones de alterna barajamos tres situaciones.

Situación A con posibilidad de crimpar cable


- Conector IEC-C14
La toma de tierra irá con cable crimpado directo a la toma de tierra de la fuente de alimentación.
Los otros dos terminales irán conectados a los terminales de entrada del interruptor, también con cable crimpado.
Una de las salidas del interruptor irá conectada a la entrada del pulsador de emergencia. También se conectará la salida del pulsador de emergencia a la entrada L de la fuente de alimentación.
La salida del interruptor restante irá conectada directamente a la entrada N de la fuente de alimentación.

Situación B con posibilidad de soldar cable:
En el caso de no contar con material para crimpar los terminales, se podrá optar por soldar la conexiones del conector e interruptor; ya que el pulsador de emergencia y la fuente de alimentación llevarán los cables atornillados.

Situación C sin posibilidad de soldar/ crimpar cable.

Si no se dispone de herramientas para soldar ni crimpar se cableará directamente a la fuente pasando solo la fase por la seta de emergencia:


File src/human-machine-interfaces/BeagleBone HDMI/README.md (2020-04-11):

## Beagle Bone 
Durante el desarrollo de los primeros prototipos de Reespirator 23, a petición del médico se realizó un interfaz gráfico para visualizar las señales del dispositivo y permitir el cambio de parámetros fácilmente. 

El desarrollo inicial consistió en visualizar los datos en un PC a través del puerto serie. Prácticamente al mismo tiempo se realizó paralelamente un desarrolo en Python que se implementó en una pantalla TFT Táctil de 7" de la marca Waveshare.

Beaglebone

Vídeo de las pruebas con la pantalla TFT Vídeos de pruebas con la pantalla TFT

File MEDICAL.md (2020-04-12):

## Información médica básica del dispositivo Reespirator 2020

El dispositivo se está diseñando para intentar cumplir los siguientes modos de funcionamiento:

**Modo controlado**
La máquina suple totalmente la ventilación del paciente pudiendo controlar tanto el volumen como la presión, sensando la medida contrapuesta.

En caso de encontrarnos en la modalidad de control por presión, los parámetros a controlar son la presión inspiratoria máxima, o PIP, (10 - 60 cmH2O), la frecuencia respiratoria (3 - 35 respiraciones por minuto) y la presión positiva al final de la espiración, o PEEP (3 - 30 cmH2O). En este modo se realiza un sensado del volumen minuto, extrapolando con ello el volumen tidal que se está administrando con cada inspiración.

Por otro lado, en su modalidad de control por volumen, se podrán controlar los mismos parámetros antes descritos salvo la presión inspiratoria, que en este caso solo sería sensada. El volumen tidal controlable con la máquina estará entre 150 y 900 ml, lo cual implica un peso mínimo del paciente de 40kg, considerando a pacientes con peso inferior como pediátricos, los cuales quedarían fuera de las especificaciones de este dispositivo.

Por defecto, la máquina se inicia en modo controlado por presión y consigna unos valores de 12 r/min, PIP de 18 cmH2O y PEEP de 6 cmH2O.

**Modo respiración asistido invasivo**
El modo de respiración asistida (o trigger) asiste a la respiración del paciente. Cuando se detecta una respiración espontánea (fijando un umbral de caudal o presión y detectando cuándo los valores exceden ese umbral) se dispara el ciclo respiratorio.

Este sistema obliga a la instauración de un número mínimo de ventilaciones de rescate, las cuales se marcarán como frecuencia respiratoria en caso de tener activado el trigger, mecanismo con el cual se permite un sistema de rescate al trigger. El número mínimo de ventilaciones de rescate es de 3.

La variable a monitorizar será el caudal inspiratorio y el umbral por defecto viene prefijado a 3 litros por minuto, pudiendo modificarse para facilitar el disparo del trigger por parte del paciente.

**Modo respiración asistido no invasivo**
Este modelo de ventilador puede utilizarse para ventilación mecánica no invasiva, incluyendo la posibilidad de modalidad BIPAP y modalidad CPAP. 

La modalidad de BIPAP representa un aprovechamiento del sistema de trigger implementado en el sistema de respiración asistida invasiva. Este modelo es viable al utilizar flujos altos con la máquina que permiten un lavado de CO2 eficaz así como compensación de fugas.

El ventilador permite igualar los parámetros de PIP y PEEP, lo que permite la utilización del sistema como máquina de CPAP aplicando únicamente una PEEP, en esta modalidad dada la construcción de la máquina se inactiva el sistema de trigger y elimina las ventilaciones de rescate.

Modo de reclutamiento alveolar
Se establece un modo de uso mediante un botón de emergencia, destinado a realizar una operación clínica de reclutamiento alveolar. Mediante dicha maniobra, el sistema aplicará una presión constante de inspiración de 40 cmH2O durante un tiempo máximo de 40 segundos. Una vez entrado en este modo, se activará la alarma acústica pertinente. Se podrá volver al modo de funcionamiento normal, antes de los 40 segundos, a través de la interfaz táctil de la máquina, según el criterio clínico del médico usuario.

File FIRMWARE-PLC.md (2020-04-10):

## Firmware del PLC

En cuanto al software para la configuración con un PLC se ha preparado sobre un PLC Siemens 1200 y un HMI si bien se está considerando también la posibilidad de portarlo a otros sistemas.

La configuración del TIA Portal para configurar el autómata y el HMI para su programación:

En esta imagen podemos apreciar el modelo exacto del PLC SIEMENS S7 1200 1215c utilizado:

Detalle del PLC

La siguiente imagen muestra la configuración básica del HMI modelo TP700 utilizado en nuestro prototipo:

Detalle del HMI Detalle del PLC

En esta imagen mostramos la configuración de red utilizada para conectar el PLC y el HMI:

Detalle de la conexión Detalle de las conexiones entre el autómata y el HMI

Las siguientes son alguana de las imágenes del software ejecutándose en el HMI:

HMI 1

HMI 2

HMI 3

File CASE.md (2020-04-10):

## Estructura básica
Reespirator 2020 puede fabricarse como ya hemos comentado en 2 versiones diferentes. 
La caja puede fabricarse también de dos formas distintas mediante corte láser o fresado de metacrilato o madera y mediante plegado de chapa-

* La versión de [metacrilato / madera / mdf](https://gitlab.com/reespirator/reespirator2020/-/blob/master/CASE-METHACRYLATE.md) es de tipo machiembrado como la que aparece en la figura para facilitar su montaje.



* La versión de [chapa plegada](https://gitlab.com/reespirator/reespirator2020/-/blob/master/CASE-LOCK.md) tiene el siguiente aspecto:
Diagrama de bloques Caja para fabricar en chapa plegada

Los archivos para su fabricación en distintos formatos se están publicando en el directorio /files.

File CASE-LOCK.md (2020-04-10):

## Estructura básica en chapa plegada
Reespirator 2020 puede fabricarse como ya hemos comentado en 2 versiones diferentes. 

La caja puede fabricarse también de dos formas distintas mediante corte láser o fresado de metacrilato o madera y mediante plegado de chapa.

Los archivos para su fabricación mediante chapa plegada en distintos formatos se están publicando en el directorio [/files/chapa](https://gitlab.com/reespirator/reespirator2020/-/tree/master/files/chapa "files/chapa").

* La versión de chapa plegada de 1mm tiene el siguiente aspecto:

Caja completa

Otra vista de la caja completa

Carcasa superior Carcasa superior para fabricar

Carcasa superior Carcasa superior para fabricar

Anillo culo Carcasa superior para fabricar

Separador inferior Carcasa superior para fabricar

Separador superior

Laterales abatibles

Culo cubierta

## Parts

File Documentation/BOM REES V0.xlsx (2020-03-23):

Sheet: Control Arduino Mega
Id | Designator | Package | Quantity | Designation | Descripción | Farnell/RS | Cod Farnell/RS | Stock | Precio unitario | Precio artículo | Precio Total | Enlace Web | Alternativa | Alternativa | NOTA | Normativa RoHS
1 | ARDUINO1 | Arduino Mega | 1 | ARDUINO MEGA | ARDUINO Placa de Desarrollo, Arduino Mega 2560, MCU ATmega2560, 54 E/S 5V, 16 Entradas Analógicas, 4 UARTs | farnell | A000067 | 3044 | 42.650 € | 42.650 € | 42.650 € | https://es.farnell.com/arduino/a000067/arduino-mega2560-rev3-placa/dp/2212779?st=arduino%20mega
2 | Q1 | TO92-ECB | 1 | BC547 | ON SEMICONDUCTOR Transistor de Unión Bipolar Único, NPN, 45 V, 300 MHz, 500 mW, 100 mA, 110 hFE | farnell | 1017673 | 41965 | 0.277 € | 1.380 € | 1.380 € | https://es.farnell.com/on-semiconductor/bc547b/transistor-npn-to-92/dp/1017673 |  |  |  | RoHS: YES / FTALATOS: YES
3 | C2 | E1,8-4 | 1 | 100n | MULTICOMP PRO Condensador Electrolítico, 0.1 µF, 50 V, Serie MCMHR, ± 20%, Con Conexión Radial, 4 mm | farnell | 1871011 | 9086 | 0.057 € | 0.060 € | 0.060 € | https://es.farnell.com/multicomp/mcmhr50v104m4x7/conden-0-1-f-50v-20/dp/1871011 |  |  |  | RoHS: YES / FTALATOS: YES
4 | C1 | E1,8-4 | 1 | 330n | MULTICOMP PRO Condensador Electrolítico, 0.33 µF, 50 V, Serie MCMHR, ± 20%, Con Conexión Radial, 4 mm | farnell | 1871013 | 3519 | 0.057 € | 0.060 € | 0.060 € | https://es.farnell.com/multicomp/mcmhr50v334m4x7/conden-0-33-f-50v-20/dp/1871013 |  |  |  | RoHS: YES / FTALATOS: YES
5 | I2C0,I2C1,DRIVER0,DRIVER1 | 2007100 | 4 | 22-?-0405-7048 | MOLEX Conector de Cable a Placa, Ángulo Recto, 2.54 mm, 4 Contactos, Header, Serie KK 7395 | farnell | 9731628 | 11062 | 0.891 € | 1.780 € | 7.120 € | https://es.farnell.com/molex/22-05-7048/conector-macho-4pos-1-fila-2-54mm/dp/9731628?ost=22-05-7048&ddkey=https%3Aes-ES%2FElement14_Spain%2Fsearch | https://es.rs-online.com/web/p/conectores-macho-para-pcb/1732944/ |  |  | RoHS: YES / FTALATOS: YES
6 | HALL1, SENS0,SENS1,SENS2,SENS3, 3V3 | 2007069 | 6 | 22-?-0305-7038 | MOLEX Conector de Cable a Placa, Ángulo Recto, 2.54 mm, 3 Contactos, Header, Serie KK 7395 | farnell | 9731610 | 18893 | 0.765 € | 0.770 € | 4.620 € | https://es.farnell.com/molex/22-05-7038/conector-macho-3pos-1-fila-2-54mm/dp/9731610?ost=22-05-7038&ddkey=https%3Aes-ES%2FElement14_Spain%2Fsearch | https://es.rs-online.com/web/p/conectores-macho-para-pcb/1732922/ |  |  | RoHS: YES / FTALATOS: YES
7 | Alimentación. VIN1 (Opcion1) | 2007041 | 1 | 22-?-0205-7028 | MOLEX Conector de Cable a Placa, Ángulo Recto, 2.54 mm, 2 Contactos, Header, Serie KK 7395 | farnell | 9731601 | 153355 | 0.693 € | 0.690 € | 0.690 € | https://es.farnell.com/molex/22-05-7028/conector-macho-2pos-1-fila-2-54mm/dp/9731601?ost=22-05-7028&ddkey=https%3Aes-ES%2FElement14_Spain%2Fsearch | https://es.rs-online.com/web/p/conectores-macho-para-pcb/1732916/ |  |  | RoHS: YES / FTALATOS: YES
7 | Alimentación. Jack1 (Opción 2) |  | 1 |  | Conector de Alimentación DC, DC10A, Jack, 5 A, 2.1 mm, Montaje de Agujero Pasante, Soldable | farnell | 224959 | 4200 | 3.290 € | 3.29 € | 3.290 € | https://es.farnell.com/cliff-electronic-components/fc68148/toma-pcb-suministro-dc-2-1mm-pack/dp/224959 |  |  |  | RoHS: YES / FTALATOS: YES
7 | Alimentación. Clema J1 (Opción 3) |  | 1 | MC24356 | Bloque Terminal Cable a Placa, 5 mm, 2 Vías, 24 AWG, 16 AWG, Tornillo | farnell | 2396250 | 12500 | 0.340 € | 0.34 € | 0.340 € | https://es.farnell.com/multicomp/mc24356/terminal-block-wire-to-brd-2pos/dp/2396250 |  |  |  | RoHS: YES / FTALATOS: YES
8 | SW1 | PEC12_INCREMENTAL_ENCODER | 1 | EC11E15244B2 | ALPS ALPINE Codificador Rotatorio Incremental, Eje de Metal, Pulsador, 11 mm, Vertical, 30 Pasos, 15 Pulsos | farnell | 2064991 | 2770 | 3.730 € | 3.730 € | 3.730 € | https://es.farnell.com/alps/ec11e15244b2/encoder-vertical-11mm-30det-15ppr/dp/2064991?st=encoder |  | https://electronicaymas.com/encoder-y-rotativos/6184-encoder-rotativo-de-20-pasos-con-pulsador.html |  | RoHS: YES / FTALATOS: YES
9 | R5 | RTRIM3339P | 1 | 15k | 3362P-1-203LF - Trimpot, Vuelta Única, Cermet, Ajuste Superior, 20 kohm, Agujero Pasante, 1 Vueltas | farnell | 9354344 | 378 | 1.140 € | 1.140 € | 1.140 € | https://es.farnell.com/bourns/3386f-1-153lf/trimmer-pot-15kohm-10-1turn-th/dp/2328522?pf=515527787%2C510232765%2C512049769 |  |  |  | RoHS: YES / FTALATOS: YES
10 | BUZZER1 | TMB12A05 | 1 | TMB12A05 | MULTICOMP PRO Transductor, 3 V a 8 V, 85 dB, Sirena, 40 mA, Orificio Pasante | farnell | 2098836 | 9694 | 1.770 € | 1.770 € | 1.770 € | https://es.farnell.com/pro-signal/abt-414-rc/transductor-electro-mech-audio/dp/2098836 | https://solectroshop.com/product-spa-624-3x-Zumbador-5V-Buzzer-Activo-4-a-7V-DC.html | https://www.amazon.es/Ociodual-Zumbador-Electronica-Arduino-Prototipos/dp/B078842JDS |  | RoHS: YES / FTALATOS: YES
11 | REGULADOR1 | LINEAR_TO220H | 1 | LINEAR_7812T | STMICROELECTRONICS Regulador Lineal de Tensión Fija Positiva, 19V a 35V de Entrada, 12V y 1.5A de Salida, TO-220-3 | farnell | 9756124 | 17024 | 0.382 € | 1.910 € | 1.910 € | https://es.farnell.com/stmicroelectronics/l7812cv/ic-v-reg-12v-7812-to-220-3/dp/9756124 |  |  |  | RoHS: YES / FTALATOS: YES
12 | LCD1 | L2034-T | 1 | 204A-BC-BC | Display Monocromo LCD Displaytech, Alfanumérico, retroiluminación LED, Transflectivo, 4 filas x 20 caracteres | RS | 532-6802 | 1600 | 23.300 € | 23.300 € | 23.300 € | https://es.rs-online.com/web/p/displays-monocromos-lcd/5326802/?searchHistory=%7B%22enabled%22%3Atrue%7D |  |  |  | RoHS: Y-EX / FTALATOS: YES
13 | H1,H2,H3,H4 | HOLES_3,6 | 4 | HOLES_MOUNT-HOLE3.6 | ETTINGER Separador, Chapado en Níquel, Latón, M3, Hembra Hexagonal, 10 mm, 10 mm | farnell | 1466761 | 17779 | 0.314 € | 1.260 € | 5.040 € | https://es.farnell.com/ettinger/05-03-103/separador-niquel-m3-x-10/dp/1466761 | https://es.rs-online.com/web/p/espaciadores/0606765/ |  |  | RoHS: YES / FTALATOS: YES
14 | R6 | R_Axial_DIN0414_L11.9mm_D4.5mm_P15.24mm_Horizontal | 1 | 10R | Resistencia de Agujero Pasante, 10 ohm, Serie MFP, 1 W, ± 5%, Axial, 350 V | farnell | 1565339 | 27000 | 0.140 € | 0.140 € | 0.140 € | https://es.farnell.com/tt-electronics-welwyn/mfp1-10r-ji/res-10r-5-1w-axial-pel-c-metal/dp/1565339?st=resistencia%201w |  |  |  | RoHS: YES / FTALATOS: YES
15 | C3 | C_Rect_L7.0mm_W3.5mm_P5.00mm | 1 | 100nF | KEMET Condensador de Película DC, 0.1 µF, 50 V, PPS Metalizado, ± 5%, Serie SMR, Caja Radial | farnell | 2529164 | 481 | 0.961 € | 4.810 € | 4.810 € | https://es.farnell.com/kemet/smr5104j50j01l16-5cbulk/conden-0-1-f-50v-5-pps-radial/dp/2529164 |  |  |  | RoHS: YES / FTALATOS: YES
16 | R7 | R_Axial_DIN0207_L6.3mm_D2.5mm_P7.62mm_Horizontal | 1 | 10R | MULTICOMP PRO Resistencia de Agujero Pasante, 10 ohm, Serie MF25, 250 mW, ± 1%, Axial, 250 V | farnell | 9341145 | 42744 | 0.036 € | 0.360 € | 0.360 € | https://es.farnell.com/multicomp/mf25-10r/res-10r-1-250mw-axial-pel-c-metal/dp/9341145 |  |  |  | RoHS: YES / FTALATOS: YES
17 | R1 | R_Axial_DIN0207_L6.3mm_D2.5mm_P7.62mm_Horizontal | 1 | 1k | MULTICOMP PRO Resistencia de Agujero Pasante, 1 kohm, Serie MF25, 250 mW, ± 1%, Axial, 250 V | farnell | 9341102 | 424750 | 0.036 € | 0.360 € | 0.360 € | https://es.farnell.com/multicomp/mf25-1k/res-1k-1-250mw-axial-pel-c-metal/dp/9341102 |  |  |  | RoHS: YES / FTALATOS: YES
18 | R2,R3,R4 | R_Axial_DIN0207_L6.3mm_D2.5mm_P7.62mm_Horizontal | 3 | 10k | MULTICOMP PRO Resistencia de Agujero Pasante, 10 kohm, Serie MF25, 250 mW, ± 1%, Axial, 250 V | farnell | 9341110 | 561368 | 0.036 € | 0.360 € | 0.360 € | https://es.farnell.com/multicomp/mf25-10k/res-10k-1-250mw-axial-pel-c-metal/dp/9341110 |  |  |  | RoHS: YES / FTALATOS: YES
19 | D1 | DO-204AL | 1 | 1N4007-E3/54 | Diodo de Recuperación Estándar, 1 kV, 1 A, Único, 1.1 V, 30 A | farnell | 2547224 | 19900 | 0.179 € | 0.18 € | 0.179 € | https://es.farnell.com/vishay/1n4007-e3-54/rectificador-est-ndar-1a-1kv-do/dp/2547224?st=1n4007 |  |  |  | RoHS: YES / FTALATOS: YES
20 | SPI0, SPI1 |  | 2 |  | MOLEX Conector de Cable a Placa, Ángulo Recto, 2.54 mm, 6 Contactos, Header, Serie KK 7395 | farnell | 9731644 | 22000 | 1.120 € | 1.12 € | 2.240 € | https://es.farnell.com/molex/22-05-7068/conector-macho-6pos-1-fila-2-54mm/dp/9731644
21 | Tornillos LCD |  | 8 | Tornillos LCD | Tornillo para Máquina, Arandela Elástica, M3, 6 mm, Acero 4.8, Zinc, Pozidriv Cabeza Alomada | farnell | 2494538 | 7700 | 0.080 € | 0.08 € | 0.640 € | https://es.farnell.com/ettinger/81-58-322/tornillo-pozi-cab-alom-acero-m3/dp/2494538
22 | Tira Pines Simple (10) |  | 1 | 22-28-5101 | Conector de Placa a Placa, 2.54 mm, 10 Contactos, Header, KK 254 42375 Series, Agujero Pasante | farnell | 3049555 | 2415 | 0.396 € | 0.43 € | 0.432 € | https://es.farnell.com/molex/22-28-4100/conector-macho-10pos-1fila-2-54mm/dp/3049537
23 | Tira Pines Dobles 1X36 |  | 2 | 22-28-4161 | Conector de Placa a Placa, 2.54 mm, 16 Contactos, Header, KK 254 42375 Series, Agujero Pasante | farnell | 3049545 | 5539 | 0.72 € | 0.72 € | 0.630 € | https://es.farnell.com/molex/22-28-4161/conector-macho-16pos-1fila-2-54mm/dp/3049545?ost=22-28-4161&ddkey=https%3Aes-ES%2FElement14_Spain%2Fsearch
24 | Tira Pines Simple (8) |  | 5 | 22-28-4084 | Conector de Placa a Placa, 2.54 mm, 8 Contactos, Header, KK 254 42375 Series, Agujero Pasante | farnell | 3049536 | 5425 | 0.62 € | 0.62 € | 3.105 € | https://es.rs-online.com/web/p/conectores-hembra-para-pcb/7655705/
25 | Tira Pines macho-macho LCD |  | 1 | 22-28-4161 | 22-28-4161 - Conector de Placa a Placa, 2.54 mm, 16 Contactos, Header, KK 254 42375 Series, Agujero Pasante | farnell | 3049545 | 5539 | 0.72 € | 0.72 € | 0.720 € | https://es.farnell.com/molex/22-28-4161/conector-macho-16pos-1fila-2-54mm/dp/3049545
26 | Tira pines hembra para LCD (16 pin) |  | 1 | SSW-116-01-T-S | SSW-116-01-T-S - Conector de Placa a Placa, 2.54 mm, 16 Contactos, Receptáculo, SSW Series, Agujero Pasante, 1 Filas | farnell | 2748581 | 280 | 1.15 € | 1.15 € | 1.150 € | https://es.farnell.com/samtec/ssw-116-01-t-s/conector-hembra-16-pos-1-fila/dp/2748581
27 | Tira de pin hembra pada LCD oled (4 pin) |  | 1 | SSW-104-01-T-S | Conector hembra para PCB Samtec Vertical 4 pines 1 fila filas paso 2.54mm Montaje Orificio Pasante Terminación Soldada | RS | 155-7911 | 360 | 0.70 € | 0.70 € | 0.699 € | https://es.rs-online.com/web/p/conectores-hembra-para-pcb/1557911/
 |  |  |  |  | TOTAL PRODUCTOS |  | 103.130 €
 |  |  |  |  | Entrega |  | 12.000 €
 |  |  |  |  | IVA (21%) |  | 24.177 €
 |  |  |  |  | Total |  | 139.307 €

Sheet: Alimentacion+Sensores+Motor
Id | Designator | Package | Quantity | Designation | Proveedor | Proveedor | Existencias | Nota
No está en Esquema | Sensor barométrico | BMP280 |  | BMP280 | https://www.mouser.es/productdetail/bosch-sensortec/bmp280?qs=QhAb4EtQfbUP9Z%252bCHM3Wyg== |  |  | ¿es esto?, o esto https://solectroshop.com/product-spa-1338-BMP280-Modulo-Sensor-de-Presion-Barometrica-de-Temperatura.html
 | Fuente alimentación 24V | LRS-350-24 |  | LRS-350-24 | https://www.mouser.es/ProductDetail/?qs=ah3jBNVE1PT%252bkwLcackrGA== |  | 830
 | Sensor Efecto Hall | KY-003 |  | KY-003
Qué tipo? | Seta Seguridad
Hace falta ? | Convertidor DC/DC
 | Jack Alimentación Arduino | Conector Jack Alimentación Macho 5,5 mm - 2,1 mm - Tornillo |  |  | https://www.electronicaembajadores.com/es/Productos/Detalle/CTD15521MT/conectores/conectores-jack-alimentacion/conector-jack-alimentacion-macho-5-5-mm-2-1-mm-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 | https://www.electronicaembajadores.com/es/Productos/Detalle/CTD15521MRC/conectores/conectores-jack-alimentacion/conector-jack-alimentacion-macho-5-5-mm-2-1-mm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 | 85-151
 | Driver TB6600 |  |  | HY-DIV268N-5A / TB6600- 3.5A
Cuáles? | Shield Sensores | Extensión Nano V3.0. Sólo versión Nano
17 o 23? | Motor Nema 17-23 |  |  | 57HS76-2804 |  |  |  | he visto en el foro que los nema 17 pueden tener poca fuerza. este nema 23 tiene 19,27Kg/cm, 2.8A Muy poco stock de nema23
 | Conector IEC-C14 con interruptor y fusible |  |  |  | https://www.electronicaembajadores.com/es/Productos/Detalle/CTBA14P8/conectores/conectores-iec-60320/conector-iec-60320-c14-chasis-macho-con-portafusible-e-in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 | https://es.rs-online.com/web/p/filtros-iec/1230296?matchtype=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 | 153
Búsqueda de stock por componentes
BMP280 | Sensor barométrico | sitio | stock | plazo de envío | fecha de comprobación de stock
 | https://solectroshop.com/product-spa-1338-BMP280-Modulo-Sensor-de-Presion-Barometrica-de-Temperatura.html | solectroshop |  | 1d
 | Fuente alimentación 24V | sitio | stock | plazo de envío | fecha de comprobación de stock
 | https://solectroshop.com/product-spa-1195-Fuente-de-Alimentacion-24V-15A-360W.html#close | solectroshop |  | 1d |  |  |  | versión 15A
 | https://solectroshop.com/product-spa-1215-Fuente-de-Alimentacion-DC-24V-5A-120W.html#close | solectroshop |  | 1d |  |  |  | versión 5A
KY-003 | Sensor Efecto Hall | sitio | stock | plazo de envío | fecha de comprobación de stock
 | https://solectroshop.com/product-spa-1388-Modulo-Sensor-de-Efecto-Hall-KY-003-con-SH3144E-TO-92.html | solectroshop |  | 1d
 | https://www.ebay.es/itm/Arduino-KY-003-Sensor-Modulo-Campo-Magnetico-Efecto-Hall/254290028521 | safetyprice ebay |  | 4d
 | Seta Seguridad | sitio | stock | plazo de envío | fecha de comprobación de stock
 | https://es.rs-online.com/web/p/botones-pulsadores-de-parada-de-emergencia/3308587/ | RS | 500 | 1d | 2020-03-23
 | Convertidor DC/DC | sitio | stock | plazo de envío | fecha de comprobación de stock
 | https://www.ebay.es/itm/Convertidor-Regulador-de-Tension-DC-DC-Converter-Arduino-5A-75W-Pantalla-XL4015/292639576949 |  |  | mas de 1semana
 | Driver TB6600 | sitio | stock | plazo de envío | fecha de comprobación de stock
 | https://solectroshop.com/product-spa-1710-TB6600-CNC-Enrutador-1-Eje-Controlador-Motor-Paso-a-Paso-Driver-5A-Impresora.html | solectroshop |  | 1d |  |  |  | es la versión de 5A
 | https://satkit.com/cnc-tb6600-driver-controlador-para-motor-paso-paso-hasta-4a?search=tb6600 | satkit | 29 | 1d
 | https://www.tuakii.com/EN-Controller-Stepper-Motors-Drivers-TB6600-4A-driver?search=tb6600 | tuakii |  | 2d
 | Shield Sensores | sitio | stock | plazo de envío | fecha de comprobación de stock
 | https://solectroshop.com/product-spa-841-Escudo-de-la-Tarjeta-de-Extension-Nano-V3-0-ATmega328P.html | solectroshop |  | 1d
 | Motor Nema 17-23 | sitio | stock | plazo de envío | fecha de comprobación de stock
 | https://solectroshop.com/product-spa-738-Motor-PAP-Nema-23-19-3kg-57HS762804.html#close | solectroshop |  | 1d
 | Conector IEC-C14 con interruptor y fusible
 | https://es.rs-online.com/web/p/conectores-iec/3521803/ | RS | 1800 | 1d varios, 2d 1800 | 2020-03-21

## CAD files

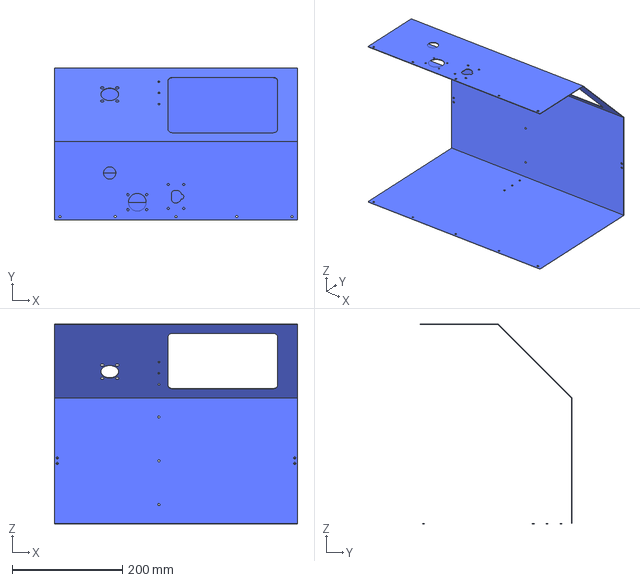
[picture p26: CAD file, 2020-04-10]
files/chapa/bmr_001_carcasa_superior_para_fabricar.igs
440.0 x 275.0 x 362.0 mm

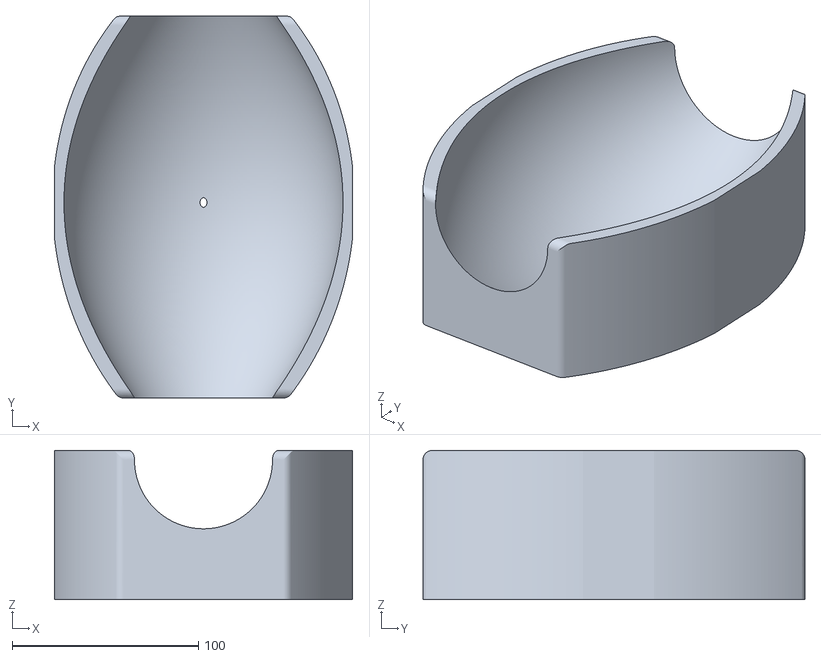
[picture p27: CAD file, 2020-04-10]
files/stl/cuna.stl
160.0 x 205.0 x 80.0

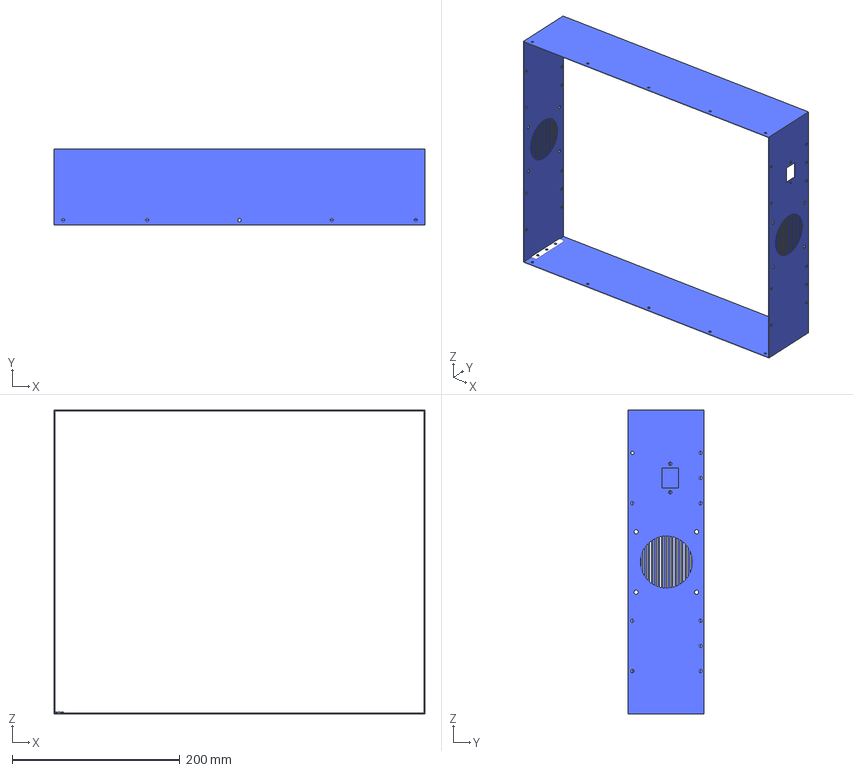
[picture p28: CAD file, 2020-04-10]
files/chapa/bmr_003_anillo_culo_para_fabricar_con_rejilla.igs
442.0 x 91.0 x 362.0 mm

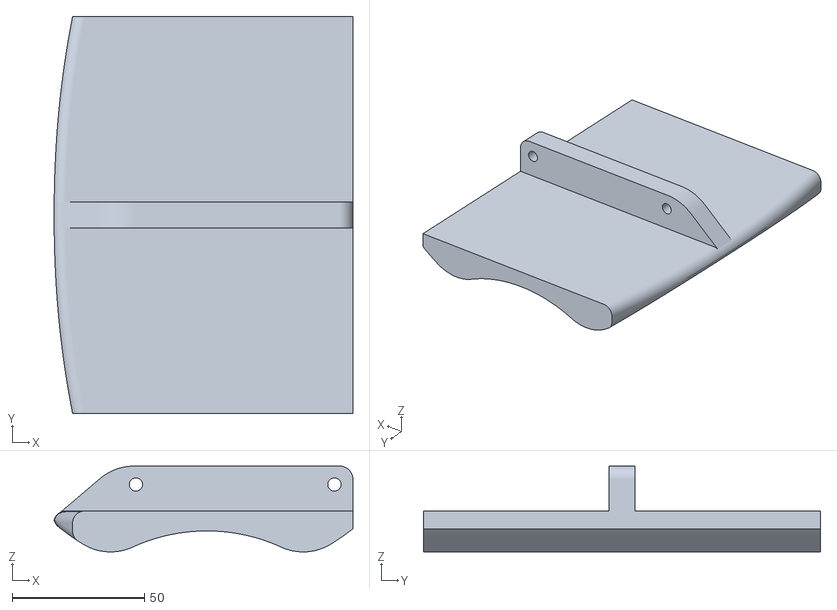
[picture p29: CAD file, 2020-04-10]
files/stl/empujador_v3.stl
112.9 x 150.0 x 32.4

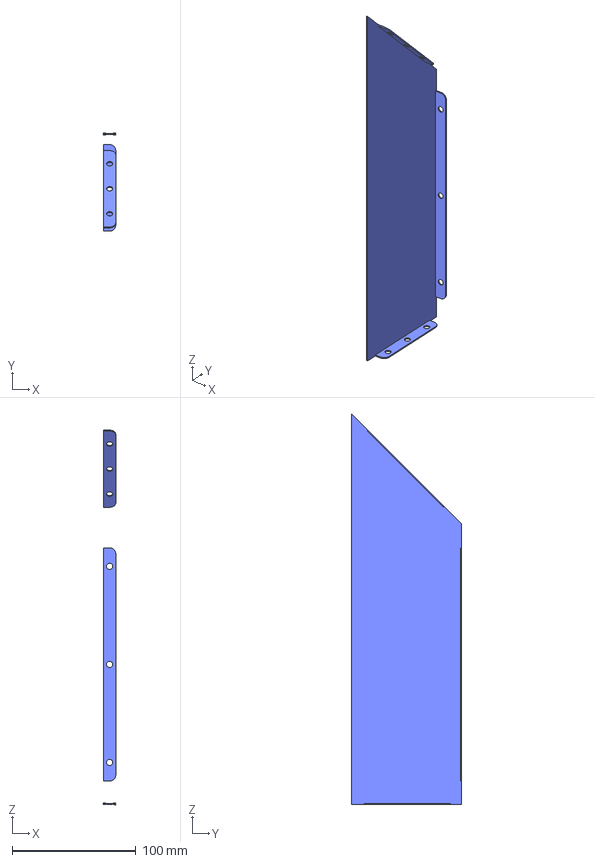
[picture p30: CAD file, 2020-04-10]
files/chapa/bmr_005_separador_superior_para_fabricar.igs
11.0 x 89.0 x 316.2 mm

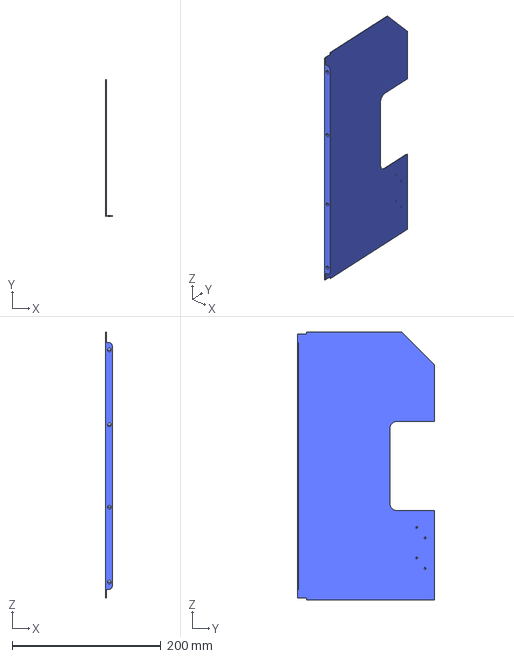
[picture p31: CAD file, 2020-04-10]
files/chapa/bmr_004_separador_inferior_para_fabricar.igs
9.00 x 184.0 x 360.0 mm

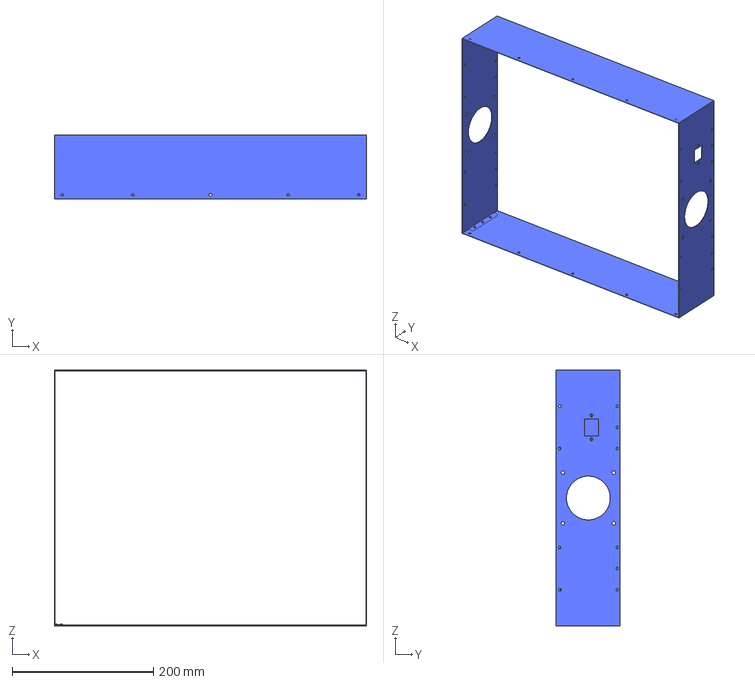
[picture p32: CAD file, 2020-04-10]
files/chapa/bmr_003_anillo_culo_para_fabricar_sin_rejilla.igs
442.0 x 91.0 x 362.0 mm

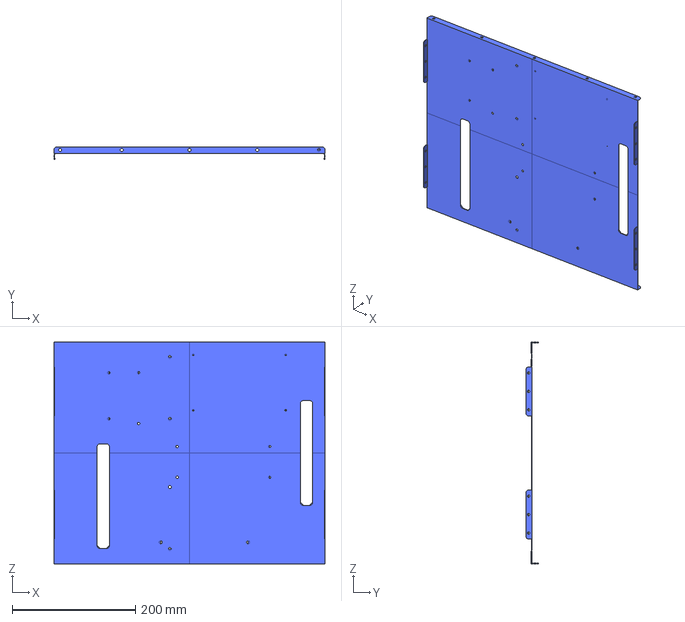
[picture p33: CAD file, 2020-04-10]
files/chapa/bmr_007_culo_cubierta_para_fabricar.igs
440.0 x 20.0 x 360.0 mm

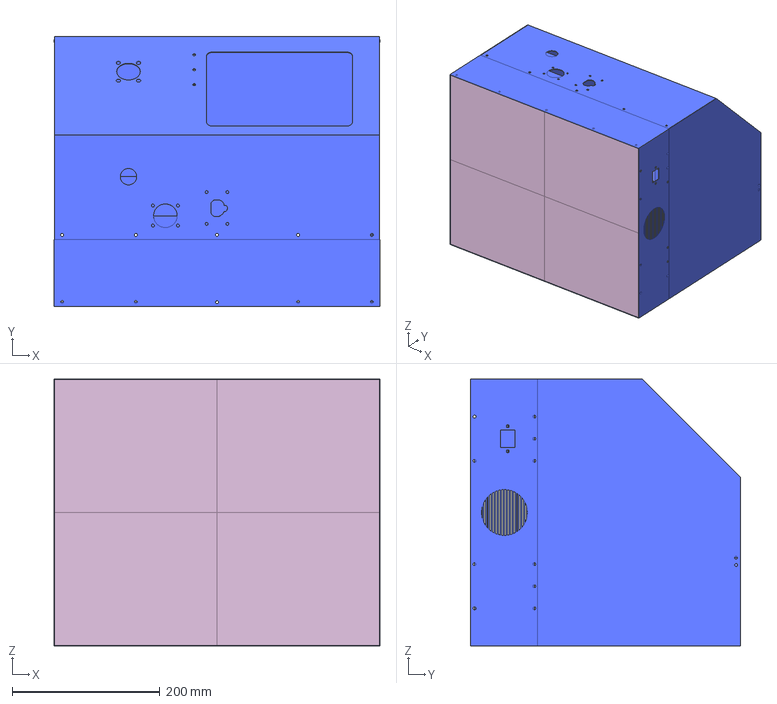
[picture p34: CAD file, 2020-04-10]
files/chapa/bmr_000_completo_para_fabricar.igs
442.0 x 366.0 x 362.0 mm

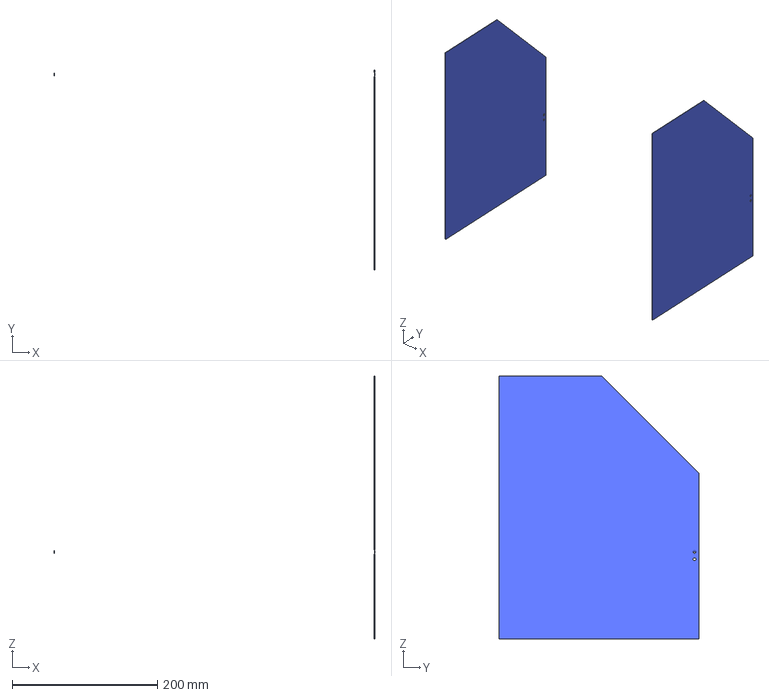
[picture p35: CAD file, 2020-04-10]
files/chapa/bmr_006_laterales_abatibles_para_fabricar.igs
442.0 x 275.0 x 362.0 mm

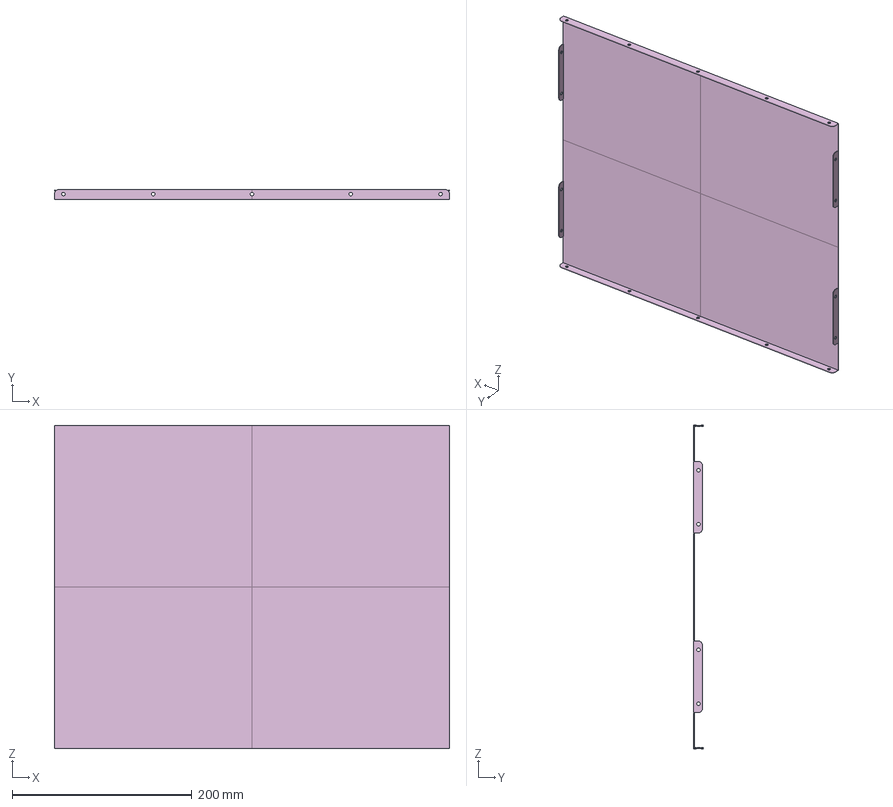
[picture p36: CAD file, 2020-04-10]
files/chapa/bmr_002_tapa_culo_para_fabricar.igs
440.0 x 11.0 x 360.0 mm

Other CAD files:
files/chapa/bmr_008_taladros_ventilador_cajon_inferior.igs

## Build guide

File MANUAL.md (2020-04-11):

## Manual de instrucciones

**Abreviaturas**

+ PIP (Peak Inspiratory Pressure), aplicación de una presión positiva al patrón de ventilación espontánea normal. Es una respiración espontánea con PEEP. Es una modalidad de soporte parcial.
+ PEEP (Positive End-Expiratory Pressure), técnica mecánica que se utiliza al ventilar a un paciente. Dicha técnica incluye el agregado de una cantidad de presión en los pulmones al final de cada respiración.
+ FR, Frecuencia de trabajo del respirador
+ VOL, volumen pulmonar de trabajo.

## Introducción
*El sistema Reespirator 2020 se puede construir en diferentes versiones por tanto su uso también difiere un poco en función del modelo.*

Las últimas versiones cuentan con un interfaz de usuario táctil, simple y de sencillo manejo gracias a los botones de gran tamaño, que permiten controlar los parámetros de operativa en las diferentes situaciones que así lo requieran, aunque no es un requisito para hacer funcionar el dispositivo, los médicos agradecen la posibilidad de visualizar la forma de las ondas de funcionamiento del mismo, por eso se ha implementado también la opción de monitorizar dichas señales en un ordenador o dispositivo externo conectado por puerto serie, cuando no se puede utilizar una pantalla integrada en el dispositivo.

Por eso está prevista la utilización de uno o varios encoder y algunos botones dónde la opción de la pantalla sea más complicada de conseguir, pero manteniendo la opción de visualización externa comentada.

Gracias a la orientación de la pantalla, en los dispositivos en los que esta está integrada, así como a la tonalidad y contraste empleados es posible supervisar el estado del paciente sin necesidad de estar muy cerca de este.

En los siguientes apartados del presente documento se muestran en detalle las opciones de operativa de Reespirator.

**Interfaz de usuario**

Como se ha indicado en el apartado introductorio del presente documento, el interfaz de usuario de Reespirator cuenta con una botonera de gran tamaño para permitir realizar las acciones que se requieran por el equipo médico. Adicionalmente, existen dos grandes apartados dentro de la ventana de trabajo:

* Visualización gráfica de estado, permite visualizar la progresión de los parámetros de flujo y presión del respirador.
* Ventana de información, muestra, dependiendo de la opción pulsada:
    - La información actual de trabajo del respirador
    - Los parámetros de configuración del respirador

Las siguientes capturas de pantalla muestran estos bloques claramente diferenciados:

    Interfaz de Usuario de Reespirator 23 con información de trabajo

    Interfaz de Usuario de Reespirator 23 con parámetros de configuración

## Menú de navegación
El menú de opciones de Reespirator cuenta únicamente con dos botones de acción:
* **INICIO**: muestra los valores numéricos de presión, flujo y volumen en tiempo real.
* **CONF**: muestra los parámetros de configuración de Reespirator 

# Parámetros de configuración
Pulsando sobre el botón **CONF** se visualizan los parámetros de configuración de
Reespirator, los cuales se indican a continuación:
* **PIP** (cmH2O), permite establecer el valor de trabajo. El rango comprendido está entre 1 y 79
* **PEEP** (cmH2O), al igual que el caso de PIP, establece el valor de trabajo con un rango comprendido entre 0 y 78, teniendo que ser siempre menor que el valor de PIP.
* **FR** (rpm), con un rango comprendido entre 1 y 30 permite establecer la frecuencia de trabajo.

# Información en tiempo real
Al iniciar Reespirator se muestran los valores de funcionamiento en tiempo real. Estos parámetros de funcionamiento, que se detallan a continuación, se refrescan cada 100 milisegundos:
* PIP (cmH2O). Peak Inspiratory Pressure
* PEEP (cmH2O). Positive End-Expiratory Pressure
* FR (rpm). Frecuencia de Trabajo
* VOL (ml). Cantidad de Aire con el que está trabajando Reespirator

Asimismo, en esta ventana de parámetros, se permite activar el Modo Recruit en el respirador, el cual permite realizar el aumento transitorio de la presión transpulmonar aplicada para reclutar alvéolos en el pulmón colapsado. Seguidamente se detalla el modo de trabajo en reespirator.

**Modo de reclutamiento**
Como ya se ha indicado, el modo Recruit permite realizar un aumento transitorio de la presión transpulmonar aplicada para re-airear el pulmón colapsado. Para activar esta funcionalidad, simplemente basta con tocar en la pantalla sobre el botón **RECRUIT**.
Tras activarse, el botón anteriormente presionado cambia a color rojo y el texto de este cambia a STOP RECRUIT,
para permitir detener la operación.
Debido al concepto de transitoriedad, en Reespirator el tiempo máximo de la operación de Recruit está configurado
a un máximo de 40 segundos. Es decir que si, transcurrido este tiempo no se desactiva manualmente, Reespirator lo hará automáticamente.

**Visualización gráfica**
Reespirator muestra de forma gráfica y en tiempo real los niveles de Presión y Flujo respectivamente. El tiempo total de ciclo que se muestra en ambas gráficas es de un minuto, tiempo suficiente para poder visualizar la evolución más reciente del paciente.
Los rangos de visualización de gráficas son:
+ Presión: entre 0 y 50 cmH2O
+ Flujo: entre -20 y 30 litros por minuto

Visualización de Gráficas de Presión y Flujo en Tiempo Real

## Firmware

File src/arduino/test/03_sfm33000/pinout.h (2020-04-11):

#ifndef PINOUT_H
#define PINOUT_H

#include "Arduino.h"

//Display

#define LCD_ROWS 2
#define LCD_COLS 16

#ifdef I2C  //i2c

//D irección de LCD I2C
#define I2C_DIR 0x3F

#else

// pines Display parallel  // parallel
#define LCD_RS A0
#define LCD_RW A1
#define LCD_E  A2
#define LCD_D4 A3
#define LCD_D5 A4
#define LCD_D6 A5
#define LCD_D7 A6

#endif // I2C

// Rotary encoder
#define CLKpin 9
#define DTpin 3
#define SWpin 2

#define ENpin 8
// Stepper driver (FlexyStepper)
#define PIN_STEPPER_STEP 6
#define MOTOR_STEP_PIN PIN_STEPPER_STEP
#define PIN_STEPPER_DIRECTION 7
#define MOTOR_DIRECTION_PIN PIN_STEPPER_DIRECTION


// Buzzer
#define BUZZpin 11

// Sensor hall
#define ENDSTOPpin 21

// Solenoid pine
#define SOLENOIDpin 39

// BME280 SPI al menos para Arduino Nano o Mega 128
// #define BMP_SCK  13
// #define BMP_MISO 12
// #define BMP_MOSI 11
// #define BMP_CS1  10 // sensor de presion 1
// #define BMP_CS2  4  // sensor de presion 2

// BME280 SPI para Arduino Mega 256
#define BMP_SCK  52
#define BMP_MISO 50
#define BMP_MOSI 51
#define BMP_CS1  53 // sensor de presion 1
#define BMP_CS2  49 // sensor de presion 2

#endif // ENCODER_H

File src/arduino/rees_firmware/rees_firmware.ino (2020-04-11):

/**
 * @file rees_firmware.ino
 * @author Reesistencia Team
 * @brief 
 * @version 0.1
 * @date 2020-03-29
 * 
 * @copyright GPLv3
 * 
 */

/**
 * Dependencies
 */

#include "defaults.h"
#include "calc.h"
#include "Sensors.h"
#include "MechVentilation.h"

#include "src/AutoPID/AutoPID.h"
#include "src/FlexyStepper/FlexyStepper.h"
#include "src/TimerOne/TimerOne.h"
#include "src/TimerThree/TimerThree.h"

/**
 * Variables
 */

#if DEBUG_STATE_MACHINE
volatile String debugMsg[15];
volatile byte debugMsgCounter = 0;
#endif

FlexyStepper *stepper = new FlexyStepper();
Sensors *sensors;
AutoPID *pid;
MechVentilation *ventilation;

VentilationOptions_t options;

/**
 * Read commands
 */

void readIncomingMsg(void)
{
    char msg[100];
    Serial2.readStringUntil('\n').toCharArray(msg, 100);
    int pip, peep, fr;
    if (String(msg).substring(0, 6) == "CONFIG")
    {
        int rc = sscanf(msg, "CONFIG PIP %d", &pip);
        if (rc == 1)
        {
            ventilation->setPeakInspiratoryPressure(pip);
        }
        else
        {
            int rc = sscanf(msg, "CONFIG PEEP %d", &peep);
            if (rc == 1)
            {
                ventilation->setPeakEspiratoryPressure(peep);
            }
            else
            {
                int rc = sscanf(msg, "CONFIG BPM %d", &fr);
                if (rc == 1)
                {
                    ventilation->setRPM(fr);
                }
            }
        }
    }
    else if (String(msg).substring(0, 7) == "RECRUIT")
    {
        uint8_t tmp = 255;
        int rc = sscanf(msg, "RECRUIT %d", &tmp);
        switch (tmp)
        {
        case 0:
            Serial.println("ACK 0");
            ventilation->deactivateRecruitment();
            break;
        case 1:
            Serial.println("ACK 1");
            ventilation->activateRecruitment();
            break;
        default:
            break;
        }
    }
}

/**
 * Setup
 */

void setup()
{
    // Puertos serie
    Serial.begin(115200);
    Serial2.begin(115200);
    Serial.println(F("Setup"));

    // Zumbador
    pinMode(PIN_BUZZ, OUTPUT);
    digitalWrite(PIN_BUZZ, HIGH); // test zumbador
    delay(100);
    digitalWrite(PIN_BUZZ, LOW);

    // FC efecto hall
    pinMode(PIN_STEPPER_ENDSTOP, INPUT_PULLUP); // el sensor de efecto hall da un 1 cuando detecta

    // Solenoid
    pinMode(PIN_SOLENOID, OUTPUT);

    // Sensores de presión
    sensors = new Sensors();
    int check = sensors->begin();
#if 0
    if (check) {
        if (check == 1) {
            Serial.println(F("Could not find sensor BME280 number 1, check wiring!"));
        } else if (check == 2) {
            Serial.println(F("Could not find sensor BME280 number 2, check wiring!"));
        }
        while (1);
    }
#endif

    // PID
    pid = new AutoPID(PID_MIN, PID_MAX, PID_KP, PID_KI, PID_KD);
    // if pressure is more than PID_BANGBANG below or above setpoint,
    // output will be set to min or max respectively
    pid->setBangBang(PID_BANGBANG);
    // set PID update interval
    pid->setTimeStep(PID_TS);

    // Parte motor
    pinMode(PIN_STEPPER_EN, OUTPUT);
    digitalWrite(PIN_STEPPER_EN, HIGH);

    // TODO: Añadir aquí la configuarcion inicial desde puerto serie

    options.height = DEFAULT_HEIGHT;
    options.sex = DEFAULT_SEX;
    options.respiratoryRate = DEFAULT_RPM;
    options.peakInspiratoryPressure = DEFAULT_PEAK_INSPIRATORY_PRESSURE;
    options.peakEspiratoryPressure = DEFAULT_PEAK_ESPIRATORY_PRESSURE;
    options.triggerThreshold = DEFAULT_TRIGGER_THRESHOLD;
    options.hasTrigger = false;

    ventilation = new MechVentilation(
        stepper,
        sensors,
        pid,
        options
    );

    Serial.println("Tiempo del ciclo (seg):" + String(ventilation->getExsuflationTime() + ventilation->getInsuflationTime()));
    Serial.println("Tiempo inspiratorio (mseg):" + String(ventilation->getInsuflationTime()));
    Serial.println("Tiempo espiratorio (mseg):" + String(ventilation->getExsuflationTime()));

    // TODO: Esperar aqui a iniciar el arranque desde el serial

    // Habilita el motor
    digitalWrite(PIN_STEPPER_EN, LOW);

    // Relay and stepper driver alarm
    // pinMode(PIN_RELAY, OUTPUT);
    // digitalWrite(PIN_RELAY, LOW);
    // pinMode(PIN_STEPPER_ALARM, INPUT_PULLUP);

    // configura la ventilación
    ventilation->start();
    ventilation->update();

    delay(1000);

    sensors->readPressure();

    //TODO: Option: if (Sensores ok) { arranca timer3 }
    Timer3.initialize(50); //50us
    Timer3.attachInterrupt(timer3Isr);

    // TODO: Make this period dependant of TIME_BASE
    // TIME_BASE * 1000 does not work!!
    // Timer1.initialize(50000); // 50 ms
    Timer1.initialize(20000);
    Timer1.attachInterrupt(timer1Isr);

    // attachInterrupt(digitalPinToInterrupt(PIN_STEPPER_ALARM), driverAlarmIsr, FALLING);
}

/**
 * Loop
 */

void loop()
{
    unsigned long time;
    time = millis();
    unsigned long static lastReadSensor = 0;
    unsigned long static lastSendConfiguration = 0;
    State static lastState;

    if (time > lastSendConfiguration + TIME_SEND_CONFIGURATION)
    {
        Serial2.print(F("CONFIG "));
        Serial2.print(ventilation->getPeakInspiratoryPressure());
        Serial2.print(F(" "));
        Serial2.print(ventilation->getPeakEspiratoryPressure());
        Serial2.print(F(" "));
        Serial2.println(ventilation->getRPM());
        lastSendConfiguration = time;

        // Check volume sensor
        if (sensors->stalledVolumeSensor())
        {
            Serial.println("Rebooting");
            sensors->rebootVolumeSensor();
        }
    }

    if (time > lastReadSensor + TIME_SENSOR)
    {
        sensors->readPressure();
        SensorPressureValues_t pressure = sensors->getRelativePressureInCmH2O();

        sensors->readVolume();
        SensorVolumeValue_t volume = sensors->getVolume();

        char string[100];
        sprintf(string, "DT %05d %05d %05d %06d", ((int)pressure.pressure1), ((int)pressure.pressure2), volume.volume, ((int)(sensors->getFlow() * 1000)));
        Serial2.println(string);
        // Serial.println(string);

        if (pressure.state == SensorStateFailed)
        {
            //TODO sensor fail. do something
            Serial.println(F("FALLO Sensor"));
            // TODO: BUZZ ALARMS LIKE HELL
        }
        if (volume.state == SensorStateFailed)
        {
            Serial.println("Fallo CRC sensor volumen");
        }
        lastReadSensor = time;

        /*
         * Notify insufflated volume
         */
        if (ventilation->getState() != lastState)
        {
            SensorLastPressure_t lastPressure = sensors->getLastPressure();
            if (ventilation->getState() == Init_Exsufflation)
            {
                Serial2.println("EOC " + String(lastPressure.maxPressure) + " " +
                                String(lastPressure.minPressure) + " " + String(volume.volume));
                sensors->resetPressures();
                sensors->resetVolumeIntegrator();
            }
            else if (ventilation->getState() == State_Exsufflation)
            {
                if (lastState != Init_Exsufflation)
                {
                    Serial2.println("EOC " + String(lastPressure.maxPressure) + " " +
                                    String(lastPressure.minPressure) + " " + String(volume.volume));
                    sensors->resetPressures();
                    sensors->resetVolumeIntegrator();
                }
            }
        }
        lastState = ventilation->getState();
    }

    if (Serial2.available())
    {
        readIncomingMsg();
    }

#if DEBUG_STATE_MACHINE
    if (debugMsgCounter)
    {
        for (byte i = 0; i < debugMsgCounter; i++)
        {
            Serial.println(debugMsg[i]);
        }
        debugMsgCounter = 0;
    }
#endif
}

void timer1Isr(void)
{
    ventilation->update();
}

void timer3Isr(void)
{
    stepper->processMovement();
}

// void driverAlarmIsr(void)
// {
//     digitalWrite(PIN_SOLENOID, SOLENOID_OPEN);
//     digitalWrite(PIN_RELAY, HIGH);
//     delayMicroseconds(60000);
//     delayMicroseconds(60000);
//     delayMicroseconds(60000);
//     digitalWrite(PIN_RELAY, LOW);
//     delayMicroseconds(60000);
//     delayMicroseconds(60000);
//     delayMicroseconds(60000);
//     ventilation->setState(State_Homing);
//     digitalWrite(PIN_BUZZ, HIGH); // test zumbador
//     delayMicroseconds(60000);
//     digitalWrite(PIN_BUZZ, LOW);
// }

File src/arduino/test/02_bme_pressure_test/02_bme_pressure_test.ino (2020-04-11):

/***************************************************************************
  This is a library for the BME280 humidity, temperature & pressure sensor

  Designed specifically to work with the Adafruit BME280 Breakout
  ----> http://www.adafruit.com/products/2650

  These sensors use I2C or SPI to communicate, 2 or 4 pins are required
  to interface. The device's I2C address is either 0x76 or 0x77.

  Adafruit invests time and resources providing this open source code,
  please support Adafruit andopen-source hardware by purchasing products
  from Adafruit!

  Written by Limor Fried & Kevin Townsend for Adafruit Industries.
  BSD license, all text above must be included in any redistribution
  See the LICENSE file for details.
 ***************************************************************************/

#include "src/Adafruit_BME280/Adafruit_BME280.h"

// BME280 SPI al menos para Arduino Nano o Mega 128
// #define BMP_SCK  13
// #define BMP_MISO 12
// #define BMP_MOSI 11
// #define BMP_CS1  10 // sensor de presion 1
// #define BMP_CS2  4  // sensor de presion 2

// BME280 SPI para Arduino Mega 256
#define BMP_SCK  52
#define BMP_MISO 50
#define BMP_MOSI 51
#define BMP_CS1  53 // sensor de presion 1
#define BMP_CS2  49 // sensor de presion 2



#define SEALEVELPRESSURE_HPA (1013.25)

Adafruit_BME280 bme1(
  BMP_CS1,
  BMP_MOSI,
  BMP_MISO,
  BMP_SCK
);
Adafruit_BME280 bme2(
  BMP_CS2,
  BMP_MOSI,
  BMP_MISO,
  BMP_SCK
);

unsigned long delayTime;

void setup() {
    Serial.begin(9600);
    while(!Serial);    // time to get serial running
    // Serial.println(F("BME280 test"));

    unsigned status1;
    unsigned status2;

    // default settings
    status1 = bme1.begin();  
    // You can also pass in a Wire library object like &Wire2
    // status = bme.begin(0x76, &Wire2)
    if (!status1) {
        Serial.print("Could not find a valid BME280 sensor in position 1, check wiring, address, sensor ID!; CS Pin:"); Serial.println(BMP_CS1);
        Serial.print("SensorID was: 0x"); Serial.println(bme1.sensorID(),16);
        Serial.print("        ID of 0xFF probably means a bad address, a BMP 180 or BMP 085\n");
        Serial.print("   ID of 0x56-0x58 represents a BMP 280,\n");
        Serial.print("        ID of 0x60 represents a BME 280.\n");
        Serial.print("        ID of 0x61 represents a BME 680.\n");
        while (1) delay(10);
    }


    status2 = bme2.begin();
    Serial.print("SensorID was: 0x"); Serial.println(bme2.sensorID(),16);
    if (!status2) {
        Serial.print("Could not find a valid BME280 sensor in position 2, check wiring, address, sensor ID!; CS Pin:"); Serial.println(BMP_CS2);
        Serial.print("SensorID was: 0x"); Serial.println(bme2.sensorID(),16);
        Serial.print("        ID of 0xFF probably means a bad address, a BMP 180 or BMP 085\n");
        Serial.print("   ID of 0x56-0x58 represents a BMP 280,\n");
        Serial.print("        ID of 0x60 represents a BME 280.\n");
        Serial.print("        ID of 0x61 represents a BME 680.\n");
        while (1) delay(10);
    }


    bme1.setSampling(Adafruit_BME280::MODE_NORMAL,     // Operating Mode.
                      Adafruit_BME280::SAMPLING_NONE,     // Temp. oversampling
                      Adafruit_BME280::SAMPLING_X16,    // Pressure oversampling
                      Adafruit_BME280::SAMPLING_NONE,   // humidity sampling
                      Adafruit_BME280::FILTER_OFF,      // Filtering.
                      Adafruit_BME280::STANDBY_MS_0_5); // Standby time.
    
    // Serial.println("-- Setting sampling BME280_1--");

    bme2.setSampling(Adafruit_BME280::MODE_NORMAL,     // Operating Mode.
                      Adafruit_BME280::SAMPLING_NONE,     // Temp. oversampling
                      Adafruit_BME280::SAMPLING_X16,    // Pressure oversampling
                      Adafruit_BME280::SAMPLING_NONE,   // humidity sampling
                      Adafruit_BME280::FILTER_OFF,      // Filtering.
                      Adafruit_BME280::STANDBY_MS_0_5); // Standby time.
    
    // Serial.println("-- Setting sampling BME280_2--");
    
    delayTime = 1000;

    // Serial.println();
}


void printValues1() {

    Serial.println("-- Default Test BME280_1--");
    Serial.print("Temperature BME280_1 = ");
    Serial.print(bme1.readTemperature());
    Serial.println(" *C");

    Serial.print("Pressure BME280_1 = ");

    Serial.print(bme1.readPressure() / 100.0F);
    Serial.println(" hPa");

    Serial.print("Approx. Altitude BME280_1 = ");
    Serial.print(bme1.readAltitude(SEALEVELPRESSURE_HPA));
    Serial.println(" m");

    Serial.print("Humidity BME280_1 = ");
    Serial.print(bme1.readHumidity());
    Serial.println(" %");

    Serial.println();

}

void printValues2() {
    Serial.println("-- Default Test BME280_2--");
    Serial.print("Temperature BME280_2 = ");
    Serial.print(bme2.readTemperature());
    Serial.println(" *C");

    Serial.print("Pressure BME280_2 = ");

    Serial.print(bme2.readPressure() / 100.0F);
    Serial.println(" hPa");

    Serial.print("Approx. Altitude BME280_2 = ");
    Serial.print(bme2.readAltitude(SEALEVELPRESSURE_HPA));
    Serial.println(" m");

    Serial.print("Humidity BME280_2 = ");
    Serial.print(bme2.readHumidity());
    Serial.println(" %");

    Serial.println();
}
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

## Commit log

2020-03-19 Documentación desde el repositorio de software
    [Pinout Arduino NANO.xlsx]
2020-03-19 reorganizando contenido de carpetas
    [Pinout Arduino NANO.xlsx]
2020-03-19 migrando archivos desde el repo soft
2020-03-21 Actualizada PCB y esquemático. Se ha cambiado un transistor y retocado alguna pista (por Antonio Ruiz)
2020-03-23 Actualizada PCB y Esquematico por Antonio Ruiz (@antoniorn1). Actualizada Documentación por Iván Torres (@itorres1). Actualizado BOM por Joaquín Cubillo
    [022057038.stp, 022057048.stp, 22057028.stp, BOM REES V0.xlsx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]
2020-03-23 Añadido equipo de desarolladores
2020-03-23 Fabrication files added
    [Reespirator23 - Reespirator23.stp-1 Base_23.stp-1.STL, Reespirator23 - Reespirator23.stp-1 NEMA23 57BYGH627.stp-1.STL, Reespirator23 - Reespirator23.stp-1 Piez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]
2020-03-23 Actualizado BOM y créditos
    [BOM REES V0.xlsx]
2020-03-24 PCB Silkscreen modified
    [REES-B_Mask.gbs, REES-B_SilkS.gbo, REES-Bottom.gbl, REES-Edge_Cuts.gm1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]
2020-04-03 Update Documentation/old/BOM REES V0.xlsx, Documentation/old/Block diagram Reespirator.jpg, Documentation/old/Documentación REESpirator final.pdf, Documentation/old/Esquema de conexion.pptx files Del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
    [BOM REES V0.xlsx, Reespirator23 - Reespirator23.stp-1 Base_23.stp-1.STL, Reespirator23 - Reespirator23.stp-1 NEMA23 57BYGH627.stp-1.STL, Reespirator23 - Reespi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]
2020-04-03 Update enlace codigo.txt, Documentacion Reespirator23.pdf, Reespirator23v4.x_t files
    [Reespirator23v4.x_t]
2020-04-04 Update readme and clean deprecated content
    [BOM REES V0.xlsx, assembly.x_t]
2020-04-05 Creación de los documentos de cada sección
2020-04-05 Añadido manual de uso
2020-04-05 Updating electronics assembly
2020-04-05 Clean assembly repo
    Clean duplicated info from assembly repository
    [022057038.stp, 022057048.stp, 22057028.stp, EC11_Rotary_Encoder_Switched.step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]
2020-04-06 assembly file
    [assembly.x_t]
2020-04-09 Deleted old files
    [assembly.x_t]
2020-04-10 Arduino y PLC
2020-04-10 Upload New File
    [v3__PROTOTIPO__-_Arduino_Mega_2560_+_BeagleBone_+_TFT_táctil_stl_Empujadorv3.STL]
2020-04-10 update electronics arduino
2020-04-10 rename stl file
    [Empujador_v3.STL]
2020-04-10 Upload chapa files
    [bmr_000_completo_para_fabricar.igs, bmr_002_tapa_culo_para_fabricar.igs, bmr_003_anillo_culo_para_fabricar_con_rejilla.igs, bmr_003_anillo_culo_para_fabricar_s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]
2020-04-10 Update Reespirator2020 PLC v1 - SIEMENS Simatic S7-1200 CPU 1512/README.md, Reespirator2020 ARD v1 - Arduino Mega 2560/README.md, Display+ BB-SW v1 - BeagleBone with ShareWave/README.md, Display+ Lap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
2020-04-10 move design files
    [bmr_001_carcasa_superior_para_fabricar v1.step]
2020-04-10 Update case lock images
2020-04-10 Case file fix
2020-04-10 Actualizado el archivo de la carcasa superior
    [bmr_001_carcasa_superior_para_fabricar.igs]
2020-04-10 update files
    [bmr_000_completo_para_fabricar.igs, bmr_001_carcasa_superior_para_fabricar.igs]
2020-04-10 add stl files
    [cuna.stl, empujador_v3.stl]
2020-04-11 arduino reespirator23 firm
2020-04-11 Montaje de metacrilato (versión previa sin terminar)
2020-04-12 Update ARDUINO-ELECTRONICS.md, interfaz_arduino_hm.png, images/interfaz_arduino_hm.png files
